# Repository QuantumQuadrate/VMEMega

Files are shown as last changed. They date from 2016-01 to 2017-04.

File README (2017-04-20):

VMEMega is a modified ardunino mega board designed to fit into the VME system designed for Saffman lab.
It has 3 communication interfaces (USB/Serial, Ethernet, I2C over backplane) and is designed to host normal mega compatible arduino shields.

Matthew Ebert
Atom Trainers (Walker Lab) and Saffman Lab

Licenced uner the Arduino Creative Commons Share-Alike licence.

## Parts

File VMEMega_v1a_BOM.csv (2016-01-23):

Part | Value | Device | Package | Description | MF | MPN | OC_FARNELL | OC_NEWARK | PACKAGE | PROD_ID | SUPPLIER
A_PWR | 3x2M | PINHD-2X3 | 2X03 | PIN HEADER
C1 | 22p | C-EU0603-RND | C0603-ROUND | CAPACITOR, European symbol
C2 | 100n | C-EU0603-RND | C0603-ROUND | CAPACITOR, European symbol
C3 | 100n | C-EU0603-RND | C0603-ROUND | CAPACITOR, European symbol
C4 | 100n | C-EU0603-RND | C0603-ROUND | CAPACITOR, European symbol
C5 | 100n | C-EU0603-RND | C0603-ROUND | CAPACITOR, European symbol
C6 | 100n | C-EU0603-RND | C0603-ROUND | CAPACITOR, European symbol
C7 | 100n | C-EU0603-RND | C0603-ROUND | CAPACITOR, European symbol
C8 | 100n | C-EU0603-RND | C0603-ROUND | CAPACITOR, European symbol
C9 | 100n | C-EU0603-RND | C0603-ROUND | CAPACITOR, European symbol
C10 | 1u | C-EU0603-RND | C0603-ROUND | CAPACITOR, European symbol
C11 | 100n | C-EU0603-RND | C0603-ROUND | CAPACITOR, European symbol
C12 | 100n | C-EU0603-RND | C0603-ROUND | CAPACITOR, European symbol
C13 | 1u | C-EU0603-RND | C0603-ROUND | CAPACITOR, European symbol
C14 | 22p | C-EU0603-RND | C0603-ROUND | CAPACITOR, European symbol
C15 | 22p | C-EU0603-RND | C0603-ROUND | CAPACITOR, European symbol
C16 | 100n | C-EU0603-RND | C0603-ROUND | CAPACITOR, European symbol
C17 | 100n | C-EU0603-RND | C0603-ROUND | CAPACITOR, European symbol
C18 | 10u | C-USC1206 | C1206 | CAPACITOR, American symbol
C19 | 100n | C-USC0603 | C0603 | CAPACITOR, American symbol
C20 | 100n | C-USC0603 | C0603 | CAPACITOR, American symbol
C21 | 100n | C-USC0603 | C0603 | CAPACITOR, American symbol
C22 | 100n | C-USC0603 | C0603 | CAPACITOR, American symbol
C23 | 100n | C-USC0603 | C0603 | CAPACITOR, American symbol
C24 | 100p | C-USC0603 | C0603 | CAPACITOR, American symbol
C25 | 10n | C-USC0603 | C0603 | CAPACITOR, American symbol
C26 | 100n | C-EU0603-RND | C0603-ROUND | CAPACITOR, European symbol
C27 | 100n | C-EU0603-RND | C0603-ROUND | CAPACITOR, European symbol
C35 | 1u | C-EU0603-RND | C0603-ROUND | CAPACITOR, European symbol
D1 | M7 | DIODE-SMB | SMB | DIODE
D2 | CD1206-S01575 | DIODE-MINIMELF | MINIMELF | DIODE
D3 | CD1206-S01575 | DIODE-MINIMELF | MINIMELF | DIODE
F1 | MF-MSMF050-2 500mA | L-EUL1812 | L1812 | INDUCTOR, European symbol
FD1 | FIDUCIALMOUNT | FIDUCIALMOUNT | FIDUCIA-MOUNT
FD2 | FIDUCIALMOUNT | FIDUCIALMOUNT | FIDUCIA-MOUNT
FD3 | FIDUCIALMOUNT | FIDUCIALMOUNT | FIDUCIA-MOUNT
FD4 | FIDUCIALMOUNT | FIDUCIALMOUNT | FIDUCIA-MOUNT
GROUND |  | SJ | SJ | SMD solder JUMPER
IC1 | NCP1117ST50T3G | MC33269ST-3.3T3 | SOT223 | Adjustable Output Low Dropout Voltage Regulator 800 mA
IC2 | 74ABT125DB | 74ABT125DB | SSOP14 | Quad bus BUFFER, 3-state
IC3 | ATMEGA2560-16AU | ATMEGA25602560-16AU | TQFP100 | MICROCONTROLLER
IC4 | ATMEGA16U2-MU | ATMEGA16U2-MU | MLF32
IC5 | 74ABT125DB | 74ABT125DB | SSOP14 | Quad bus BUFFER, 3-state
IC6 | LP2985-33DBVR | LP2985-XXDBVR33 | SOT23-DBV | ULTRALOW-POWER 50-mA LOW-DROPOUT LINEAR REGULATORS
IC7 | LMV358IDGKR | LMV358MMX | MSOP08 | Dual General Purpose, Low Voltage, Rail-to-Rail Output Operational Amplifiers
IC9 | LP2985-33DBVR | LP2985-XXDBVR33 | SOT23-DBV | ULTRALOW-POWER 50-mA LOW-DROPOUT LINEAR REGULATORS
ICSP | 3x2M | PINHD-2X3 | 2X03 | PIN HEADER
ICSP1 | 3x2M | PINHD-2X3 | 2X03 | PIN HEADER
J1 | MAGJACK | MAGJACK | MAGJACK | RJ-45 with LEDs
J2 | POWER_JACKPTH_LOCK | POWER_JACKPTH_LOCK | POWER_JACK_PTH_LOCK | Power Jack |  |  |  |  |  | PRT-00119
JP1 |  | M081X08 | 1X08 | Header 8
JP2 |  | M081X08 | 1X08 | Header 8
JP3 |  | M081X08 | 1X08 | Header 8
JP4 |  | M081X08 | 1X08 | Header 8
JP5 | 2x2M - NM | PINHD-2X2 | 2X02 | PIN HEADER
JP7 |  | M081X08 | 1X08 | Header 8
JP8 | M10";M10"" | 1X10 | Header 10
L | YELLOW | LEDCHIP-LED0805 | CHIP-LED0805 | LED
L1 | BLM21 | WE-CBF_0805 | 0805 | SMD EMI Suppression Ferrite Beads
L2 |  | WE-CBF-7427920_0805 | 0805 | SMD EMI Suppression Ferrite Beads WE-CBF |  | 7427920 | 1635707 | 08P2358 | IND-0805 |  | Wuerth Elektronik
L3 |  | WE-CBF-7427920_0805 | 0805 | SMD EMI Suppression Ferrite Beads WE-CBF |  | 7427920 | 1635707 | 08P2358 | IND-0805 |  | Wuerth Elektronik
L4 |  | WE-CBF-74279206_0805 | 0805 | SMD EMI Suppression Ferrite Beads WE-CBF |  | 74279206 | 1635729 | 08P2376 | IND-0805 |  | Wuerth Elektronik
L5 |  | WE-CBF-7427920_0805 | 0805 | SMD EMI Suppression Ferrite Beads WE-CBF |  | 7427920 | 1635707 | 08P2358 | IND-0805 |  | Wuerth Elektronik
L6 |  | WE-CBF-7427920_0805 | 0805 | SMD EMI Suppression Ferrite Beads WE-CBF |  | 7427920 | 1635707 | 08P2358 | IND-0805 |  | Wuerth Elektronik
L7 |  | WE-CBF-7427920_0805 | 0805 | SMD EMI Suppression Ferrite Beads WE-CBF |  | 7427920 | 1635707 | 08P2358 | IND-0805 |  | Wuerth Elektronik
ON | GREEN | LEDCHIP-LED0805 | CHIP-LED0805 | LED
PC1 | 47u | CPOL-EUD | PANASONIC_D | POLARIZED CAPACITOR, European symbol
PC2 | 47u | CPOL-EUD | PANASONIC_D | POLARIZED CAPACITOR, European symbol
PC3 | 47u | CPOL-EUD | PANASONIC_D | POLARIZED CAPACITOR, European symbol
PC4 | 47u | CPOL-EUD | PANASONIC_D | POLARIZED CAPACITOR, European symbol
R1 | 1M | R-EU_R0603 | R0603-ROUND | RESISTOR, European symbol
R2 | 1M | R-EU_R0603 | R0603-ROUND | RESISTOR, European symbol
R3 | 2k/1% | R-EU_R0603 | R0603 | RESISTOR, European symbol
R4 | 100k | R-EU_R0603 | R0603 | RESISTOR, European symbol
R5 | 10k | R-EU_R0603 | R0603 | RESISTOR, European symbol
R6 | 49.9/1% | R-EU_R0603 | R0603 | RESISTOR, European symbol
R7 | 100 | R-EU_R0603 | R0603 | RESISTOR, European symbol
R8 | 100 | R-EU_R0603 | R0603 | RESISTOR, European symbol
R9 | 1.5k | R-US_R0603 | R0603 | RESISTOR, American symbol
R10 | 1.5k | R-US_R0603 | R0603 | RESISTOR, American symbol
R11 | 49.9/1% | R-EU_R0603 | R0603 | RESISTOR, European symbol
R12 | 49.9/1% | R-EU_R0603 | R0603 | RESISTOR, European symbol
R13 | 49.9/1% | R-EU_R0603 | R0603 | RESISTOR, European symbol
RESET | TS42031-160R-TR-7260 | TS42 | TS42 | TS42
RESET-EN |  | SJ | SJ | SMD solder JUMPER
RN1 | 10K | 4R-NCAT16 | CAT16 | Array Chip Resistor |  |  | unknown | unknown
RN2 | 22R | 4R-NCAY16 | CAY16 | Array Chip Resistor |  |  | unknown | unknown
RN3 | 1k | 4R-NCAY16 | CAY16 | Array Chip Resistor |  |  | unknown | unknown
RN4 | 1k | 4R-NCAY16 | CAY16 | Array Chip Resistor |  |  | unknown | unknown
RN5 | 10K | 4R-NCAT16 | CAT16 | Array Chip Resistor |  |  | unknown | unknown
RX | YELLOW | LEDCHIP-LED0805 | CHIP-LED0805 | LED
TX | YELLOW | LEDCHIP-LED0805 | CHIP-LED0805 | LED
U$1 | ENC28J60-I/SS | ENC28J60-I/SS | SOP65P780X200-28N | Stand-Alone Ethernet Controller |  | ENC28J60-I/SS | 1084620 | 31K1708 | SOP-28 |  | Microchip
U$2 | TCA9617A | TCA9617A | TSSOP-8
U$3 | LOWNOISE_VREF_V1B | LOWNOISE_VREF_V1B | LOWNOISE_VREF_V1B
U$4 | SMAJ20A | SMAJ20A | D0-214AC
U$5 | SMAJ20A | SMAJ20A | D0-214AC
U$6 | SMAJ20A | SMAJ20A | D0-214AC
U$17 | DIN_41612_PLUG | DIN_41612_PLUG | DIN_41612_PLUG
X2 | USB-B_TH | PN61729 | PN61729 | BERG USB connector
XIO | 18x2F-H8.5 | PINHD-2X18 | 2X18 | PIN HEADER
Y1 | CSTCE16M0V53-R0 16MHZ | RESONATORMU | RESONATOR
Y2 | 16MHz | XTAL/S | QS | CRYSTAL
Y3 | CSTCW25M0X53-R0 25MHZ | RESONATORMU | RESONATOR
Z1 | CG0603MLC-05E | VARISTORCN0603 | CT/CN0603 | VARISTOR
Z2 | CG0603MLC-05E | VARISTORCN0603 | CT/CN0603 | VARISTOR

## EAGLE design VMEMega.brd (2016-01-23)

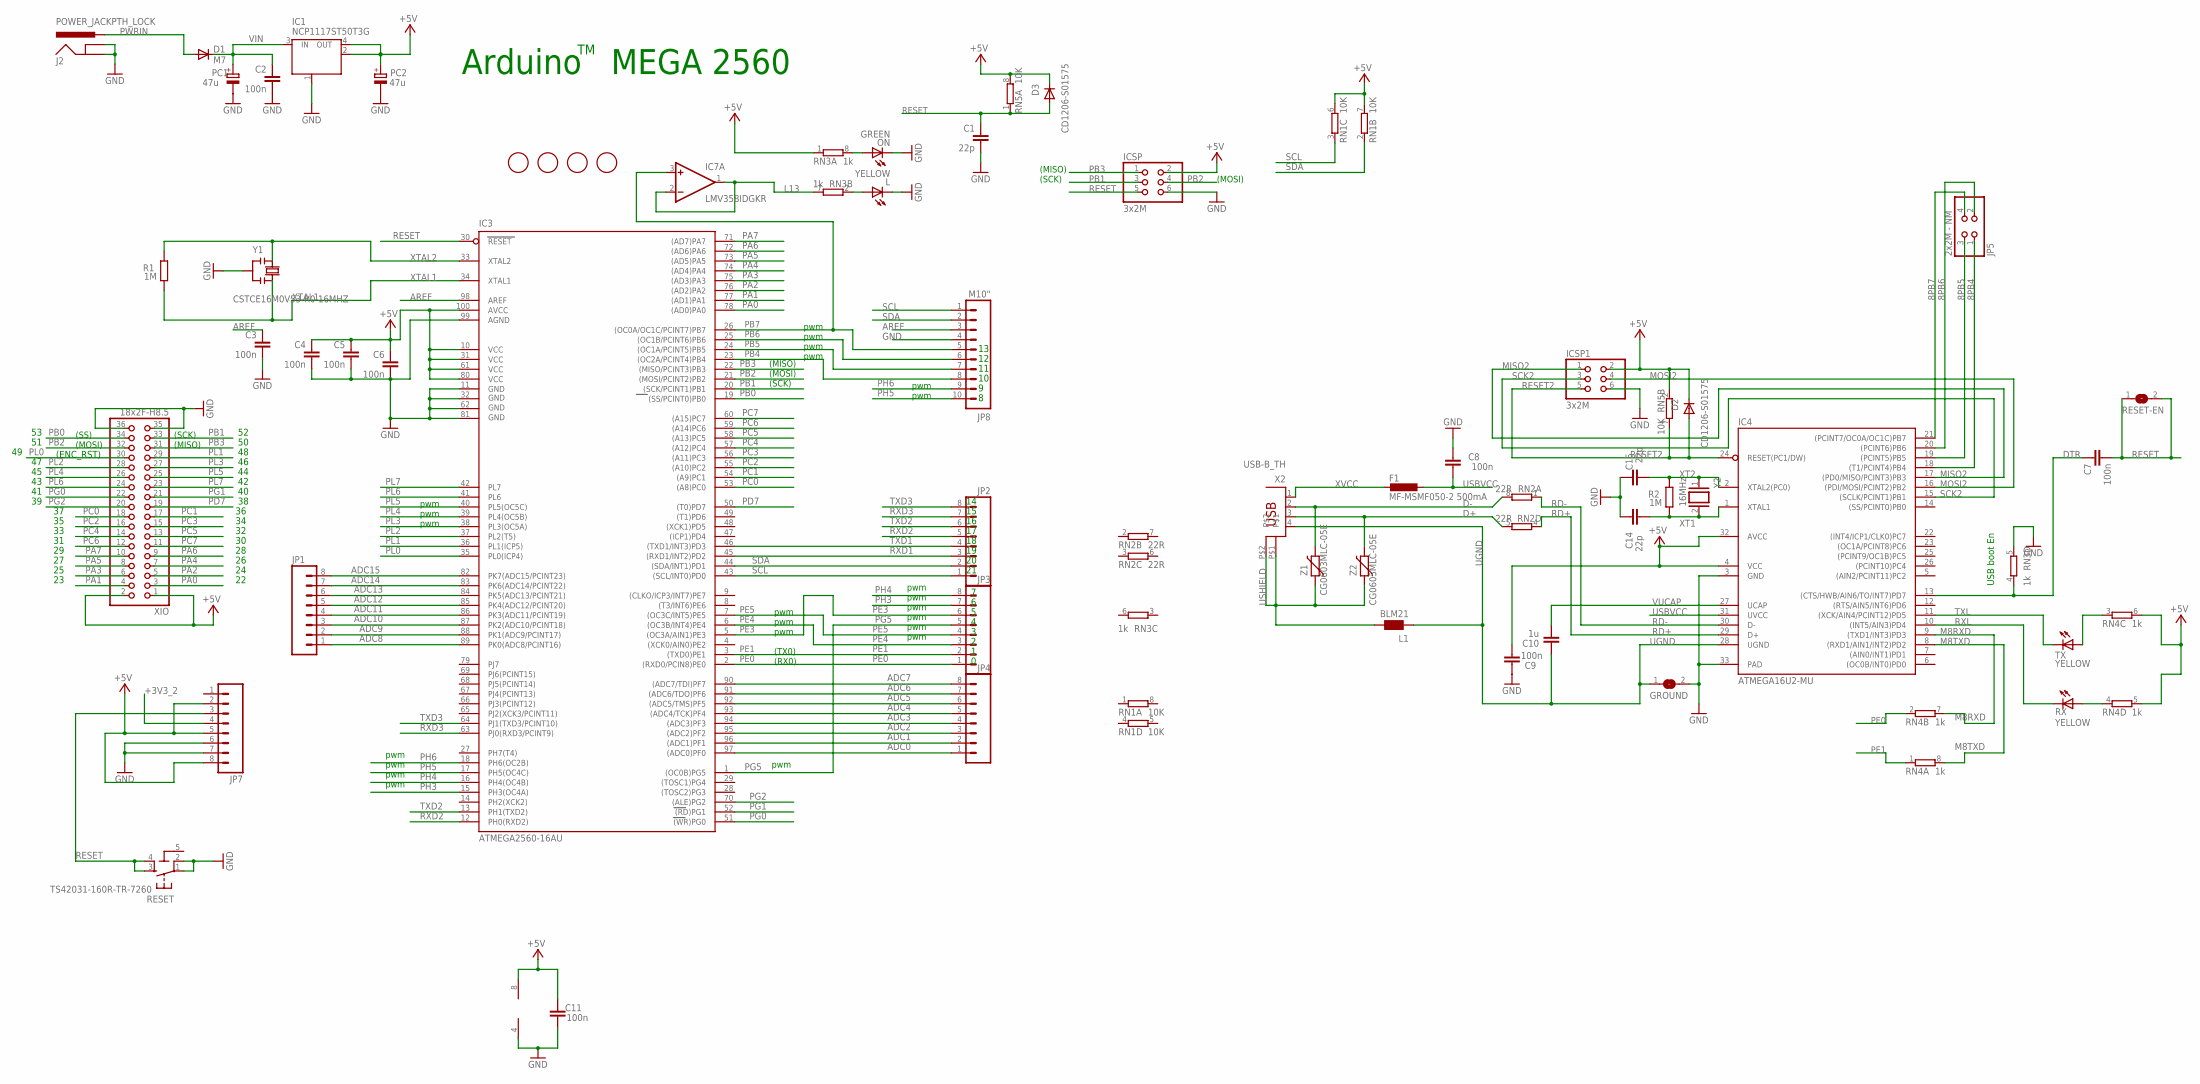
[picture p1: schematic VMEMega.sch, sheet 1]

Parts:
C1, C14, C15: 22p; C0603-ROUND
C2, C3, C4, C5, C6, C7, C8, C9, C11: 100n; C0603-ROUND
C10: 1u; C0603-ROUND
D1: M7; SMB
D2, D3: CD1206-S01575; MINIMELF
F1: MF-MSMF050-2 500mA; L1812
FD1, FD2, FD3, FD4: FIDUCIALMOUNT; FIDUCIA-MOUNT
GROUND: SJ
IC1: NCP1117ST50T3G; SOT223
IC3: ATMEGA2560-16AU; TQFP100
IC4: ATMEGA16U2-MU; MLF32
IC7: LMV358IDGKR; MSOP08
ICSP, ICSP1: 3x2M; 2X03
J2: POWER_JACKPTH_LOCK; POWER_JACK_PTH_LOCK
JP1, JP2, JP3, JP4, JP7: M081X08; 1X08
JP5: 2x2M - NM; 2X02
JP8: M10"; 1X10
L: YELLOW; CHIP-LED0805
L1: BLM21; 0805
ON: GREEN; CHIP-LED0805
PC1, PC2: 47u; PANASONIC_D
R1, R2: 1M; R0603-ROUND
RESET: TS42031-160R-TR-7260; TS42
RESET-EN: SJ
RN1, RN5: 10K; CAT16
RN2: 22R; CAY16
RN3, RN4: 1k; CAY16
RX: YELLOW; CHIP-LED0805
TX: YELLOW; CHIP-LED0805
X2: USB-B_TH; PN61729
XIO: 18x2F-H8.5; 2X18
Y1: CSTCE16M0V53-R0 16MHZ; RESONATOR
Y2: 16MHz; QS
Z1, Z2: CG0603MLC-05E; CT/CN0603

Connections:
5-GND: RESET.5 (5-GND)
8PB4: IC4.18 ((T1/PCINT4)PB4), JP5.1
8PB5: IC4.19 ((PCINT5)PB5), JP5.3
8PB6: IC4.20 ((PCINT6)PB6), JP5.2
8PB7: IC4.21 ((PCINT7/OC0A/OC1C)PB7), JP5.4
+3V3_2: JP7.4; also elsewhere on the board
+5V: C4.1, C5.1, C6.1, C9.1, C11.2, D2.C, D3.C, IC1.2 (OUT), IC1.4 (OUT), IC3.10 (VCC), IC3.31 (VCC1), IC3.61 (VCC2), IC3.80 (VCC3), IC3.100 (AVCC), IC4.4 (VCC), IC4.32 (AVCC), IC7.8 (V+), ICSP.2, ICSP1.2, JP7.2, JP7.5, JP7.8, PC2.+, RN1.6 (2), RN1.7 (2), RN3.1, RN4.5 (2), RN4.6 (2), RN5.2 (1), RN5.8 (2), XIO.1, XIO.2; also elsewhere on the board
ADC0: IC3.97 ((ADC0)PF0), JP4.1
ADC1: IC3.96 ((ADC1)PF1), JP4.2
ADC2: IC3.95 ((ADC2)PF2), JP4.3
ADC3: IC3.94 ((ADC3)PF3), JP4.4
ADC4: IC3.93 ((ADC4/TCK)PF4), JP4.5
ADC5: IC3.92 ((ADC5/TMS)PF5), JP4.6
ADC6: IC3.91 ((ADC6/TDO)PF6), JP4.7
ADC7: IC3.90 ((ADC7/TDI)PF7), JP4.8
ADC8: IC3.89 (PK0(ADC8/PCINT16)), JP1.1
ADC9: IC3.88 (PK1(ADC9/PCINT17)), JP1.2
ADC10: IC3.87 (PK2(ADC10/PCINT18)), JP1.3
ADC11: IC3.86 (PK3(ADC11/PCINT19)), JP1.4
ADC12: IC3.85 (PK4(ADC12/PCINT20)), JP1.5
ADC13: IC3.84 (PK5(ADC13/PCINT21)), JP1.6
ADC14: IC3.83 (PK6(ADC14/PCINT22)), JP1.7
ADC15: IC3.82 (PK7(ADC15/PCINT23)), JP1.8
AREF: C3.1, IC3.98 (AREF), JP8.3; also elsewhere on the board
D+: RN2.5 (2), X2.3, Z2.2
D-: RN2.8 (2), X2.2, Z1.2
DTR: C7.1, IC4.13 ((CTS/HWB/AIN6/TO/INT7)PD7), RN3.4 (1)
GND: C1.2, C2.2, C3.2, C4.2, C5.2, C6.2, C8.2, C9.2, C11.1, C14.2, C15.2, GROUND.2, IC1.1 (GND/ADJ), IC3.11 (GND), IC3.32 (GND1), IC3.62 (GND2), IC3.81 (GND3), IC3.99 (AGND), IC4.3 (GND), IC4.33 (PAD), IC7.4 (V-), ICSP.6, ICSP1.6, J2.GND, J2.GNDBREAK, JP7.6, JP7.7, JP8.4, L.C, ON.C, PC1.-, PC2.-, RESET.1, RESET.2, RN3.5 (2), XIO.35, XIO.36, Y1.2; also elsewhere on the board
L13: IC7.1 (OUT), IC7.2 (-IN), RN3.7 (2)
M8RXD: IC4.9 ((TXD1/INT3)PD3), RN4.7 (2)
M8TXD: IC4.8 ((RXD1/AIN1/INT2)PD2), RN4.8 (2)
MISO2: IC4.17 ((PD0/MISO/PCINT3)PB3), ICSP1.1
MOSI2: IC4.16 ((PDI/MOSI/PCINT2)PB2), ICSP1.4
unnamed: L.A, RN3.2 (1)
unnamed: ON.A, RN3.8 (2)
unnamed: RN4.4 (1), RX.A
unnamed: RN4.3 (1), TX.A
PA0: IC3.78 ((AD0)PA0), XIO.3
PA1: IC3.77 ((AD1)PA1), XIO.4
PA2: IC3.76 ((AD2)PA2), XIO.5
PA3: IC3.75 ((AD3)PA3), XIO.6
PA4: IC3.74 ((AD4)PA4), XIO.7
PA5: IC3.73 ((AD5)PA5), XIO.8
PA6: IC3.72 ((AD6)PA6), XIO.9
PA7: IC3.71 ((AD7)PA7), XIO.10
PB0: IC3.19 ((SS/PCINT0)PB0), XIO.34; also elsewhere on the board
PB1: IC3.20 ((SCK/PCINT1)PB1), ICSP.3, XIO.33; also elsewhere on the board
PB2: IC3.21 ((MOSI/PCINT2)PB2), ICSP.4, XIO.32; also elsewhere on the board
PB3: IC3.22 ((MISO/PCINT3)PB3), ICSP.1, XIO.31; also elsewhere on the board
PB4: IC3.23 ((OC2A/PCINT4)PB4), JP8.8
PB5: IC3.24 ((OC1A/PCINT5)PB5), JP8.7
PB6: IC3.25 ((OC1B/PCINT6)PB6), JP8.6
PB7: IC3.26 ((OC0A/OC1C/PCINT7)PB7), IC7.3 (+IN), JP8.5
PC0: IC3.53 ((A8)PC0), XIO.18
PC1: IC3.54 ((A9)PC1), XIO.17
PC2: IC3.55 ((A10)PC2), XIO.16
PC3: IC3.56 ((A11)PC3), XIO.15
PC4: IC3.57 ((A12)PC4), XIO.14
PC5: IC3.58 ((A13)PC5), XIO.13
PC6: IC3.59 ((A14)PC6), XIO.12
PC7: IC3.60 ((A15)PC7), XIO.11
PD7: IC3.50 ((T0)PD7), XIO.19
PE0: IC3.2 ((RXD0/PCIN8)PE0), JP3.1, RN4.2 (1)
PE1: IC3.3 ((TXD0)PE1), JP3.2, RN4.1
PE3: IC3.5 ((OC3A/AIN1)PE3), JP3.6
PE4: IC3.6 ((OC3B/INT4)PE4), JP3.3
PE5: IC3.7 ((OC3C/INT5)PE5), JP3.4
PG0: IC3.51 ((WR)PG0), XIO.22
PG1: IC3.52 ((RD)PG1), XIO.21
PG2: IC3.70 ((ALE)PG2), XIO.20
PG5: IC3.1 ((OC0B)PG5), JP3.5
PH3: IC3.15 (PH3(OC4A)), JP3.7
PH4: IC3.16 (PH4(OC4B)), JP3.8
PH5: IC3.17 (PH5(OC4C)), JP8.10
PH6: IC3.18 (PH6(OC2B)), JP8.9
PL0: IC3.35 (PL0(ICP4)), XIO.30; also elsewhere on the board
PL1: IC3.36 (PL1(ICP5)), XIO.29
PL2: IC3.37 (PL2(T5)), XIO.28
PL3: IC3.38 (PL3(OC5A)), XIO.27
PL4: IC3.39 (PL4(OC5B)), XIO.26
PL5: IC3.40 (PL5(OC5C)), XIO.25
PL6: IC3.41 (PL6), XIO.24
PL7: IC3.42 (PL7), XIO.23
PWRIN: D1.A, J2.PWR
RD+: IC4.29 (D+), RN2.4 (1)
RD-: IC4.30 (D-), RN2.1
RESET: C1.1, C7.2, D3.A, IC3.30 (RESET), ICSP.5, JP7.3, RESET.3, RESET.4, RESET-EN.1, RESET-EN.2, RN5.1
RESET2: D2.A, IC4.24 (RESET(PC1/DW)), ICSP1.5, RN5.7 (2)
RXD1: IC3.45 ((RXD1/INT2)PD2), JP2.3
RXD2: IC3.12 (PH0(RXD2)), JP2.5
RXD3: IC3.63 (PJ0(RXD3/PCINT9)), JP2.7
RXL: IC4.10 ((INT5/AIN3)PD4), RX.C
SCK2: IC4.15 ((SCLK/PCINT1)PB1), ICSP1.3
SCL: IC3.43 ((SCL/INT0)PD0), JP2.1, JP8.1, RN1.3 (1); also elsewhere on the board
SDA: IC3.44 ((SDA/INT1)PD1), JP2.2, JP8.2, RN1.2 (1); also elsewhere on the board
TXD1: IC3.46 ((TXD1/INT3)PD3), JP2.4
TXD2: IC3.13 (PH1(TXD2)), JP2.6
TXD3: IC3.64 (PJ1(TXD3/PCINT10)), JP2.8
TXL: IC4.11 ((XCK/AIN4/PCINT12)PD5), TX.C
UGND: C10.2, GROUND.1, IC4.28 (UGND), L1.1, X2.4
USBVCC: C8.1, F1.1, IC4.31 (UVCC)
USHIELD: L1.2, X2.P$1, X2.P$2, Z1.1, Z2.1
VIN: C2.1, D1.C, IC1.3 (IN), PC1.+
VUCAP: C10.1, IC4.27 (UCAP)
XT1: C14.1, IC4.1 (XTAL1), R2.1, Y2.2
XT2: C15.1, IC4.2 (XTAL2(PC0)), R2.2, Y2.1
XTAL1: IC3.34 (XTAL1), R1.1, Y1.3
XTAL2: IC3.33 (XTAL2), R1.2, Y1.1
XVCC: F1.2, X2.1

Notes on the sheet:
Arduino MEGA 2560
(SCK)
(MISO)
(MOSI)
pwm
(TX0)
(RX0)
(SS)
USB boot En
(ENC_RST)

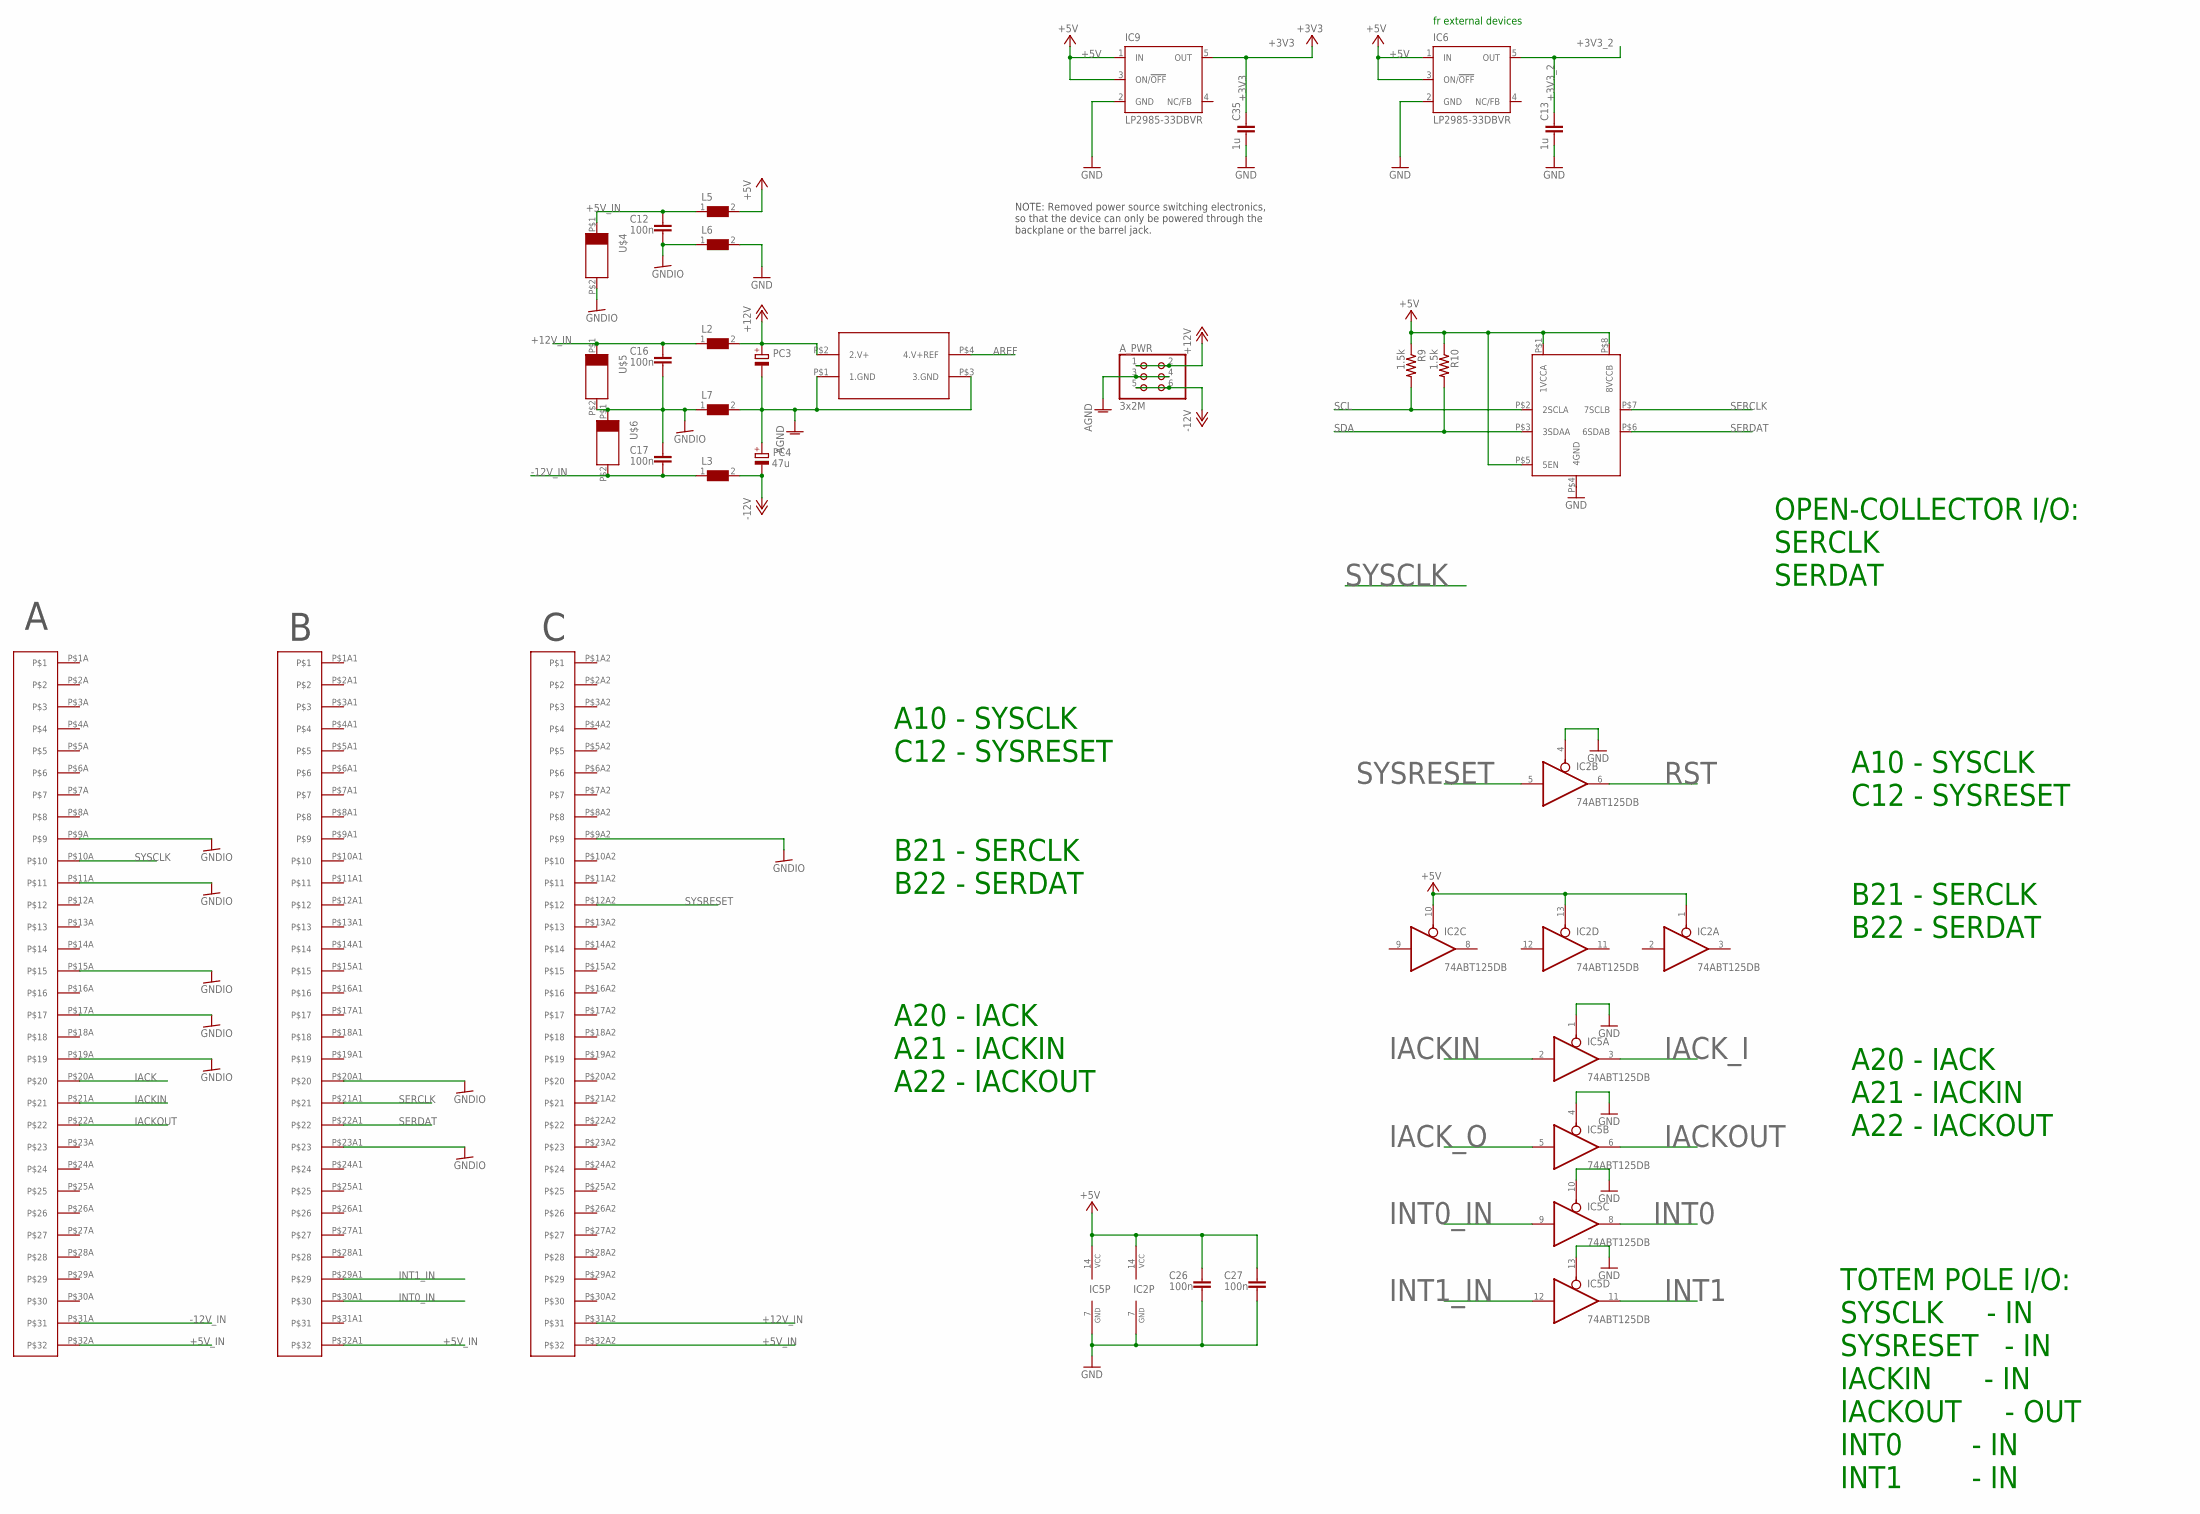
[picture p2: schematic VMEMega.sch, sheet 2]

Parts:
A_PWR: 3x2M; 2X03
C12, C16, C17, C26, C27: 100n; C0603-ROUND
C13, C35: 1u; C0603-ROUND
IC2, IC5: 74ABT125DB; SSOP14
IC6, IC9: LP2985-33DBVR; SOT23-DBV
L2, L3, L5, L6, L7: WE-CBF-7427920_0805; 0805
PC3, PC4: 47u; PANASONIC_D
R9, R10: 1.5k; R0603
U$2: TCA9617A; TSSOP-8
U$3: LOWNOISE_VREF_V1B
U$4, U$5, U$6: SMAJ20A; D0-214AC
U$17: DIN_41612_PLUG

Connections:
+3V3: C35.2, IC9.5 (OUT); also elsewhere on the board
+3V3_2: C13.2, IC6.5 (OUT); also elsewhere on the board
+5V: C26.2, C27.2, IC2.1 (OE), IC2.10 (OE), IC2.13 (OE), IC2.14 (VCC), IC5.14 (VCC), IC6.1 (IN), IC6.3 (ON/!OFF), IC9.1 (IN), IC9.3 (ON/!OFF), L5.2, R9.1, R10.1, U$2.P$1 (1VCCA), U$2.P$5 (5EN), U$2.P$8 (8VCCB); also elsewhere on the board
+5V_IN: C12.2, L5.1, U$4.P$1, U$17.P$32A, U$17.P$32A1, U$17.P$32A2
+12V: A_PWR.1, A_PWR.2, L2.2, PC3.+, U$3.P$2 (2.V+)
+12V_IN: C16.2, L2.1, U$5.P$1, U$17.P$31A2
-12V: A_PWR.5, A_PWR.6, L3.2, PC4.-
-12V_IN: C17.1, L3.1, U$6.P$2, U$17.P$31A
AGND: A_PWR.3, A_PWR.4, L7.2, PC3.-, PC4.+, U$3.P$1 (1.GND), U$3.P$3 (3.GND)
AREF: U$3.P$4 (4.V+REF); also elsewhere on the board
GND: C13.1, C26.1, C27.1, C35.1, IC2.4 (OE), IC2.7 (GND), IC5.4 (OE), IC5.7 (GND), IC5.10 (OE), IC5.13 (OE), IC6.2 (GND), IC9.2 (GND), L6.2, U$2.P$4 (4GND); also elsewhere on the board
GNDIO: C12.1, C16.1, C17.2, L6.1, L7.1, U$4.P$2, U$5.P$2, U$6.P$1, U$17.P$9A, U$17.P$9A2, U$17.P$11A, U$17.P$15A, U$17.P$17A, U$17.P$19A, U$17.P$20A1, U$17.P$23A1
IACK: U$17.P$20A
IACKIN: IC5.2 (I), U$17.P$21A
IACKOUT: IC5.6 (O), U$17.P$22A
IACK_I: IC5.3 (O)
IACK_O: IC5.5 (I)
INT0: IC5.8 (O)
INT0_IN: IC5.9 (I), U$17.P$30A1
INT1: IC5.11 (O)
INT1_IN: IC5.12 (I), U$17.P$29A1
RST: IC2.6 (O)
SCL: R9.2, U$2.P$2 (2SCLA); also elsewhere on the board
SDA: R10.2, U$2.P$3 (3SDAA); also elsewhere on the board
SERCLK: U$2.P$7 (7SCLB), U$17.P$21A1
SERDAT: U$2.P$6 (6SDAB), U$17.P$22A1
SYSCLK: U$17.P$10A
SYSRESET: IC2.5 (I), U$17.P$12A2

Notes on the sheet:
A10 - SYSCLK C12 - SYSRESET
B21 - SERCLK B22 - SERDAT
A20 - IACK A21 - IACKIN A22 - IACKOUT
TOTEM POLE I/O: SYSCLK - IN SYSRESET - IN IACKIN - IN IACKOUT - OUT INT0 - IN INT1 - IN
OPEN-COLLECTOR I/O: SERCLK SERDAT
NOTE: Removed power source switching electronics, so that the device can only be powered through the backplane or the barrel jack.
fr external devices

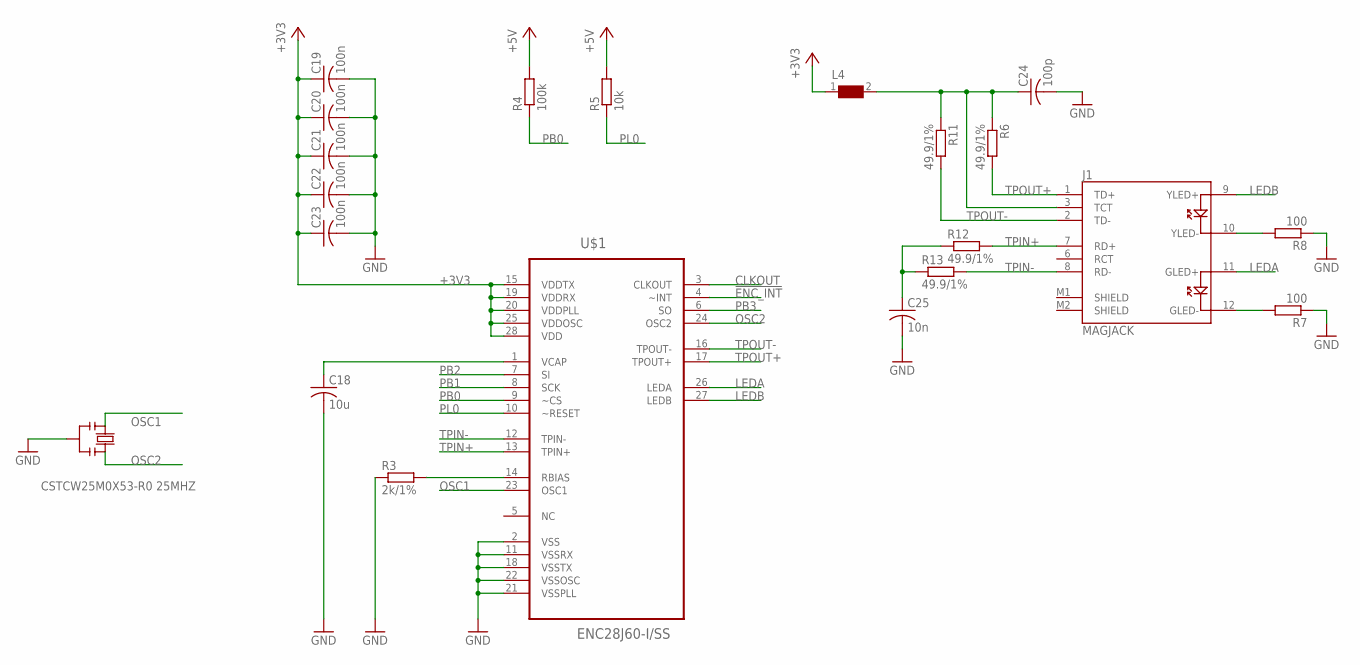
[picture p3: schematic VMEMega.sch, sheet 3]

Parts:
C18: 10u; C1206
C19, C20, C21, C22, C23: 100n; C0603
C24: 100p; C0603
C25: 10n; C0603
J1: MAGJACK
L4: WE-CBF-74279206_0805; 0805
R3: 2k/1%; R0603
R4: 100k; R0603
R5: 10k; R0603
R6, R11, R12, R13: 49.9/1%; R0603
R7, R8: 100; R0603
U$1: ENC28J60-I/SS; SOP65P780X200-28N
Y3: CSTCW25M0X53-R0 25MHZ; RESONATOR

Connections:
!ENC_INT: U$1.4 (~INT)
+3V3: C19.1, C20.1, C21.1, C22.1, C23.1, L4.1, U$1.15 (VDDTX), U$1.19 (VDDRX), U$1.20 (VDDPLL), U$1.25 (VDDOSC), U$1.28 (VDD); also elsewhere on the board
+5V: R4.2, R5.2; also elsewhere on the board
CLKOUT: U$1.3 (CLKOUT)
GND: C18.2, C19.2, C20.2, C21.2, C22.2, C23.2, C24.2, C25.2, R3.1, R7.1, R8.1, U$1.2 (VSS), U$1.11 (VSSRX), U$1.18 (VSSTX), U$1.21 (VSSPLL), U$1.22 (VSSOSC), Y3.2; also elsewhere on the board
LEDA: J1.11 (GLED+), U$1.26 (LEDA)
LEDB: J1.9 (YLED+), U$1.27 (LEDB)
unnamed: J1.12 (GLED-), R7.2
unnamed: J1.10 (YLED-), R8.2
unnamed: C25.1, R12.1, R13.1
unnamed: C24.1, J1.3 (TCT), L4.2, R6.1, R11.1
unnamed: R3.2, U$1.14 (RBIAS)
unnamed: C18.1, U$1.1 (VCAP)
OSC1: U$1.23 (OSC1), Y3.1
OSC2: U$1.24 (OSC2), Y3.3
PB0: R4.1, U$1.9 (~CS); also elsewhere on the board
PB1: U$1.8 (SCK); also elsewhere on the board
PB2: U$1.7 (SI); also elsewhere on the board
PB3: U$1.6 (SO); also elsewhere on the board
PL0: R5.1, U$1.10 (~RESET); also elsewhere on the board
TPIN+: J1.7 (RD+), R12.2, U$1.13 (TPIN+)
TPIN-: J1.8 (RD-), R13.2, U$1.12 (TPIN-)
TPOUT+: J1.1 (TD+), R6.2, U$1.17 (TPOUT+)
TPOUT-: J1.2 (TD-), R11.2, U$1.16 (TPOUT-)

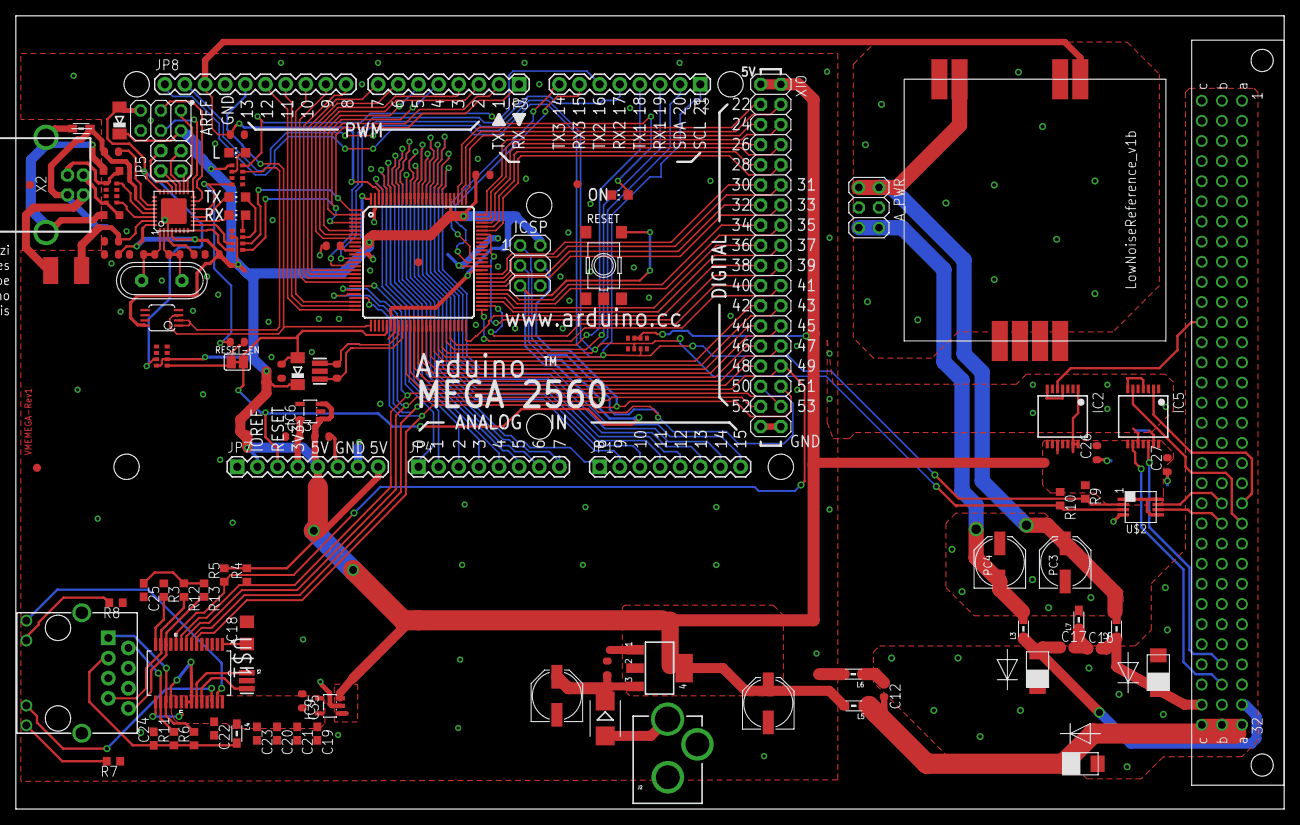
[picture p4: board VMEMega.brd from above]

Board: 2 copper layers, 160.0 x 100.1 mm, 106 parts (1 on the bottom side), 137 nets.

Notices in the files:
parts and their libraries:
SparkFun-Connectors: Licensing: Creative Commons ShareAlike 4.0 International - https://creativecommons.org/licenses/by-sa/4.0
